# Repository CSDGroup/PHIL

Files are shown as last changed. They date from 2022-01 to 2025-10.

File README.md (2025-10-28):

# PHIL

Pipetting Helper Imaging Lid – PHIL - 2021

Latest Update:
15.05.2022 - Updated Arduino Mega Shield to prevent burnouts by increasing the width of motor power traces:
https://www.pcbway.com/project/shareproject/Arduino_Mega14x_V4_3edde2c7.html

Open-source personal pipetting robots with live-cell incubation and microscopy compatibility

Overview
- personal small desktop liquid handling robot designed in AutoCAD 2018.
- small, light, cheap
- fast self-assembly from 3D printed and commercial parts
- long-term live cell culture media exchange, immunostainings, etc
- compatible with microscope stage-top use during time-lapse microscopy
- user-friendly control software

Reference

If you use PHIL please cite the following paper:

Dettinger*, Dettinger*, Kull, Arekatla, Ahmed, Zhang, Schneiter, Wehling, Schirmacher, Kawamura, Loeffler, Schroeder*
Open-source personal pipetting robots with live-cell incubation and microscopy compatibility
Nature Communications 13, 2999 (2022).
https://doi.org/10.1038/s41467-022-30643-7

System Requirements

Hardware requirements

PHILs GUI requires only a standard computer with enough RAM to support the in-memory operations.

Software requirements

OS Requirements

This package is supported for Windows and requires Matlab 2020. The package has been tested on the following systems:

Windows 10 - Matlab 2020

This project is covered under the MIT License.

Download Files
Current version
PHIL_Complete_Resources_210716.zip (ZIP, 47.2 MB)vertical_align_bottom
2021.07.16: Added companies with international shipping options to «Order_List.xlsx» in PHIL_Complete_Resources.zip

Previous versions
2021.07.05: PHIL_Complete_Resources - .zip (ZIP, 47.2 MB)vertical_align_bottom

ZIP file contents
PHIL operation
PHIL_Operation_Instructions.pdf: Complete instructions for using PHIL
PHIL_GUI_210602.m: Executable Matlab script for PHIL gui

PHIL production
Order_List.xlsx: Complete parts list for all required parts
PHIL_Print_Instructions.pdf: Full print settings of all parts
3D print files as described below
PHIL_Assembly_Instructions.pdf: Full instructions for PHIL assembly
PHIL_Arduino_MEGA_14Pump_210216.ino: Complete Arduino sketch for PHIL operation. Requires Accelstepper library installed
 
3D print files
Individual components are encoded by the individual STL files below. You can use these to print them individually.
All required components for a PHIL robot have been grouped into 10 sets for easy simultaneous printing of several components in one print session.

Set_1.stl
Body_VB1.stl: Main body of PHIL
Body_Top_VB1.stl: Frame for mounting Z-axis stepper motors
Elbow_Left_VB1.stl: Left actuator arm for mounting limit switches
Elbow_Right_VB1.stl: Right actuator arm for mounting limit switches
Hands_VB1.stl: Left and right actuator arm
Tube_Plug_VB1.stl: Tube holder for PHIL body

Set_2.stl
Arm_Plate_VB1.stl: Stepper motor mount for left and right arms
Body_Bottom_VB1.stl: Base for main body of PHIL
 
 
Set_3_100infill.stl
LR_Arm_100Infill.stl: Left and right arms for PHIL. To be printed at 100% infill

Set_4.stl
Chamber _VB1.stl: Incubator chamber
2 x Screw_VB1.stl: Screw drives for z-axis
 
 
Set_5.stl
Chamber_Lid_VB1.stl: Lid for incubator chamber
USB_Back_VB1.stl: USB cable mounting bracket, back
USB_Front_VB1.stl: USB cable mounting bracket, front
Handle_VB1.stl: Handle for power control box
Pin_Cup_V1.stl: Pipet holder for normal wells
(Pin_Cup_V1.stl can be replaced with Pin_Cup_Deep_Well_VB1.stl when working with deep well multiwell plates - see instructions)
 
 
Set_6.stl
Power_Box_Left_VB1.stl: Left half of power control box
 
 
Set_7.stl
Power_Box_Right_VB1.stl: Right half of power control box
 
 
Set_8.stl
Arduino_Plate_VB1.stl: Plate for mounting arduinos
 
 
Set_9.stl
Mount_1x_31.stl: 6x mounting brackets for peristaltic pump
 
 
Set_10.stl
Wheel_1x_31.stl: 6x rotors for peristaltic pump

The following files are not required for a PHIL, but help the production:

tube_bender_top_v2.stl: Tube bending press outer body
tube_bender_bot_v2.stl: Tube bending press inner frame
85mm_Tube_cutter_v2.stl: Jig for cutting 85mm segment of peristaltic pump tubing

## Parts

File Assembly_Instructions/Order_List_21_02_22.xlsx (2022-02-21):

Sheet: Basic Build
Order Type | Supplier | Article No. | Item | Quantity | Price | Total Price | Swiss Order | International Order
Per Robot | 3dware | 1900511.1 | NEMA 17 Stepper motor 1.8 degree, 1.5A 23mm | 4 | 16.95 | 67.8 | https://www.3dware.ch/NEMA-17-Stepper-motor-1.8-degree,-1.5A-23mm-En.htm | https://www.banggood.com/Trianglelab-or-Dforce-Nema-17-23mm-42-Motor-Titan-Stepper-Motor-4-lead-Fits-Extruder-J-head-Bowden-Reprap-for-3D-Printer-p-1845364.ht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
Per Robot | 3dware | 1900354.15 | Power Supply 24v 15A | 1 | 44.95 | 44.95 | https://www.3dware.ch/Power-Supply-24v-15A-En.htm | https://www.banggood.com/Creality-3D-24V-or-15A-Universal-Regulated-Switching-Mode-LED-Power-Supply-For-Ender-3-3D-Printer-p-1335224.html?cur_warehouse=CN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
Per Robot | 3dware | 1900320.4 | StepStick DRV8825 Stepper Motor Driver | 7 | 4.7 | 32.9 | https://www.3dware.ch/StepStick-DRV8825-Stepper-Motor-Driver-En.htm | https://www.banggood.com/Geekcreit-3D-Printer-Stepstick-DRV8825-Stepper-Motor-Driver-Reprap-4-Layer-PCB-p-920162.html?cur_warehouse=CN&rmmds=search
Per Robot | 3dware | 1900824.1 | CH Power Cord 3-pin to C13 | 1 | 5.2 | 5.2 | https://www.3dware.ch/CH-Power-Cord-3-pin-to-C13-En.htm | https://www.banggood.com/AC-Power-Supply-Adapter-Cord-Cable-Lead-3-Prong-for-Laptop-p-930564.html?cur_warehouse=CN&ID=3426&rmmds=search
Per Robot | 3dware | 1900816.3 | Panel mount USB data cable USB type B ma | 1 | 4.7 | 4.7 | https://www.3dware.ch/Panel-mount-USB-data-cable-USB-type-B-male-to-female-50cm-En.htm | https://www.amazon.com/Printer-Extension-Adapter-Connections-Scanner/dp/B071P2BGK5?s=electronics
Per Robot | 3dware | 1900853.1 | Power socket with fuse with wire 10A 250 | 1 | 5.7 | 5.7 | https://www.3dware.ch/Power-socket-with-fuse-with-wire-10A-250V-En.htm | https://www.banggood.com/SIMAX3D-15A-250V-Power-Switch-3pin-AC-Power-Socket-with-Fuse-for-3D-Printer-p-1724703.html?cur_warehouse=CN&ID=6287830&rmmds=search
Per Robot | 3dware | 1900502.6 | NEMA 17 Stepper motor 1.8 degree, 1.5A | 3 | 30.45 | 91.35 | https://www.3dware.ch/NEMA-17-Stepper-motor-1.8-degree,-1.5A-En.htm | https://www.banggood.com/JKM-NEMA17-1_842-Hybrid-Stepper-Motor-Two-Phase-60mm-7_3kg_cm-1_7A-Step-Motor-p-1274866.html?cur_warehouse=CN&rmmds=search
Per Robot | Distrelec | 143-83-920 | Male PCB Header, 36 Contacts, 2.54mm Pitch | 5 | 1.67 | 8.35 | https://www.distrelec.ch/en/890-straight-male-pcb-header-through-hole-rows-36-contacts-54mm-pitch-preci-dip-890-18-036-10-803/p/14383920?track=true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 | https://www.digikey.com/en/products/detail/molex/0022285364/6167155
Per Robot | Distrelec | 135-87-326 | Micro Switch D2F, 3A, 1CO | 4 | 1.91 | 7.64 | https://www.distrelec.ch/en/micro-switch-d2f-3a-1co-47n-hinge-lever-omron-electronic-components-d2f/p/13587326?track=true&no-cache=true&marketingPopup=false | https://www.digikey.com/en/products/detail/omron-electronics-inc-emc-div/D2F-L/83251?s=N4IgTCBcDaIDoBcAiYBiBaAMiAugXyA
Per Robot | Distrelec | 30092030 | Kondensator, 100uF, 50VDC, 20% | 7 | 0.12 | 0.84 | https://www.distrelec.ch/en/radial-electrolytic-capacitor-100uf-50vdc-20-rnd-components-rnd-150ehr101m50b/p/30092030?track=true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 | https://www.digikey.com/en/products/detail/nichicon/UKL1H101MPD1TD/4317601
Per Robot | Distrelec | 30093668 | Female PCB Receptacle, 8 Contacts, 2.54mm Pitch | 14 | 0.15 | 2.1 | https://www.distrelec.ch/en/straight-female-pcb-receptacle-through-hole-rows-contacts-54mm-pitch-rnd-connect-rnd-205-00648/p/30093668?track=true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 | https://www.digikey.com/en/products/detail/sullins-connector-solutions/PPTC081LFBN-RC/810147
Per Robot | Distrelec | 30093662 | Female PCB Receptacle, 2 Contacts, 2.54mm Pitch | 4 | 0.09 | 0.36 | https://www.distrelec.ch/en/straight-female-pcb-receptacle-through-hole-rows-contacts-54mm-pitch-rnd-connect-rnd-205-00642/p/30093662?track=true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 | https://www.digikey.com/en/products/detail/sullins-connector-solutions/PPPC021LFBN-RC/810174
Per Robot | Distrelec | 300-43-058 | Wire-To-Board Terminal Block | 2 | 0.3 | 0.6 | https://www.distrelec.ch/en/wire-to-board-terminal-block-13-31mm-26-16awg-08mm-pitch-poles-rnd-connect-rnd-205-00232/p/30043058?track=true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 | https://www.digikey.com/en/products/detail/phoenix-contact/1733570/348731
Per Robot | digikey | 259-1994-ND | Sunon fans 80mm x 80mm Vapo-Bearing | 1 | 7.76 | 7.76 | https://www.digikey.ch/product-detail/de/sunon-fans/ME80202V3-000U-A99/259-1994-ND/9449330?productid=9449330 | https://www.digikey.com/en/products/detail/sunon-fans/ME80202V3-000U-A99/9449330?s=N4IgTCBcDa4KwE4C0BGBCAsSByAREAugL5A
Per Robot | rs-online.com | 612-5739 | ball bearing id 3mm od 8mm w 4mm | 27 | 5.7 | 153.9 | https://www.modellhubschrauber.ch/Ersatzteile/Elektro/T-Rex-100-760/T-Rex-450/T-Rex-450S-XL/Ersatzteile/Kugellager-693ZZ-3x8x4mm.htm?shop=helibaumann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 | https://www.amazon.com/Miniature-Bearings-Shielded-Bearing-3mm8mm4mm/dp/B0711MRFTY
Per robot | Qosina | 40101 | Female Luer Lock to1/4-28 UNF Thread Connector | 2 | 0.53 | 1.06 |  | https://www.qosina.com/female-luer-lock-connector-white-2-40101
Per 5 Robots | pcbway.com | G662950 | 14 Stepper Motor Arduino Shield | 1 | 25 | 25 |  | https://www.pcbway.com/project/shareproject/14_Stepper_Arduino_Mega_Shield.html
As Necessary | Distrelec | 301-09-228 | No-Clean Solder Wire B2.1 217°C 0.5mm | 1 | 11.18 | 11.18
As Necessary | Reichelt | SDB 2,4 SW | Heat-shrink tubing box, 15 m, black, Ø2.4 mm | 1 |  |  |  | https://www.reichelt.com/ch/en/heat-shrink-tubing-box-15-m-black-2-4-mm-sdb-2-4-sw-p53756.html?CCOUNTRY=459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
Per robot | McMASTER-CARR | 51525K271 | Luer lock to 1/16" barb tube coupling | 2 | 5.18 | 10.36 |  | https://www.mcmaster.com/51525K271/
Per robot | Ismatec | HV-05502-28 | Tygon LMT-55, 1.02 mm ID tubing | 1 | 45.26 | 45.26 |  | https://www.masterflex.com/i/ismatec-pump-tubing-tygon-lmt-55-1-02-mm-id-33-ft/0550228
As Necessary | Fisher Scientific | 11929445 | 30M PTFE TUBE 0.56 X 1.07MM 1.07MM | 1 |  |  |  | https://webshop.fishersci.com/insight2_ch/getProduct.do?productCode=11929445
Per pump | New England Small Tube Corp | NE-1310-03 | Stainless Steel Tube .025“ OD x .013“ ID x 1.00“ Long | 1 |  |  |  | https://www.nesmalltube.com/about_tubing/hypodermic.html
Per robot | Newark | 923050-TE | 23 Gauge, 0.33mm, Needle | 1 | 25.88 | 25.88 |  | https://www.newark.com/metcal/923050-te/needle-23-gauge-orange-0-33mm/dp/93K0393
Per robot | Monster Bolts |  | 8 mm M3 Flat Head Socket Cap screws | 16 |  |  |  | https://monsterbolts.com/products/socket-flat-a2-m3?variant=36305130188
Per robot | Monster Bolts |  | 10 mm M3 Flat Head Socket Cap screws | 3 |  |  |  | https://monsterbolts.com/products/socket-flat-a2-m3?variant=36305130316
Per robot | Monster Bolts |  | 16 mm M3 Flat Head Socket Cap screws | 20 |  |  |  | https://monsterbolts.com/products/socket-flat-a2-m3?variant=36305131020
Per robot | Monster Bolts |  | 10 mm M3 Socket Head Cap screws | 100 |  |  |  | https://monsterbolts.com/products/socket-cap-zn12-9-m3?variant=31330479046739
Per robot | Monster Bolts |  | 20 mm M3 Socket Head Cap screws | 20 |  |  |  | https://monsterbolts.com/products/socket-cap-zn12-9-m3?variant=31330479439955
Per robot | Monster Bolts |  | 2.4 mm thick M3 Hex Nut | 123 |  |  |  | https://monsterbolts.com/collections/nuts-and-locking-nuts/products/nuts-din934-a2?variant=36167130316
Per robot | Uxcell | US-SA-AJD-353837 | M1.5 X 10mm Stainless Steel Phillips Pan Round Head Self Tapping Screws | 8 |  |  |  | https://www.amazon.com/uxcell-Stainless-Phillips-Tapping-Screws/dp/B01KXTTT22
 |  |  |  |  |  | 552.89

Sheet: Full Build
Order Type | Supplier | Article No. | Item | Quantity | Price | Total Price | Swiss Order | International Order
Per Robot | 3dware | 1900511.1 | NEMA 17 Stepper motor 1.8 degree, 1.5A 23mm | 4 | 16.95 | 67.8 | https://www.3dware.ch/NEMA-17-Stepper-motor-1.8-degree,-1.5A-23mm-En.htm | https://www.banggood.com/Trianglelab-or-Dforce-Nema-17-23mm-42-Motor-Titan-Stepper-Motor-4-lead-Fits-Extruder-J-head-Bowden-Reprap-for-3D-Printer-p-1845364.ht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
Per Robot | 3dware | 1900354.15 | Power Supply 24v 15A | 1 | 44.95 | 44.95 | https://www.3dware.ch/Power-Supply-24v-15A-En.htm | https://www.banggood.com/Creality-3D-24V-or-15A-Universal-Regulated-Switching-Mode-LED-Power-Supply-For-Ender-3-3D-Printer-p-1335224.html?cur_warehouse=CN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
Per Robot | 3dware | 1900320.4 | StepStick DRV8825 Stepper Motor Driver | 14 | 4.7 | 65.8 | https://www.3dware.ch/StepStick-DRV8825-Stepper-Motor-Driver-En.htm | https://www.banggood.com/Geekcreit-3D-Printer-Stepstick-DRV8825-Stepper-Motor-Driver-Reprap-4-Layer-PCB-p-920162.html?cur_warehouse=CN&rmmds=search
Per Robot | 3dware | 1900824.1 | CH Power Cord 3-pin to C13 | 1 | 5.2 | 5.2 | https://www.3dware.ch/CH-Power-Cord-3-pin-to-C13-En.htm | https://www.banggood.com/AC-Power-Supply-Adapter-Cord-Cable-Lead-3-Prong-for-Laptop-p-930564.html?cur_warehouse=CN&ID=3426&rmmds=search
Per Robot | 3dware | 1900816.3 | Panel mount USB data cable USB type B ma | 1 | 4.7 | 4.7 | https://www.3dware.ch/Panel-mount-USB-data-cable-USB-type-B-male-to-female-50cm-En.htm | https://www.amazon.com/Printer-Extension-Adapter-Connections-Scanner/dp/B071P2BGK5?s=electronics
Per Robot | 3dware | 1900853.1 | Power socket with fuse with wire 10A 250 | 1 | 5.7 | 5.7 | https://www.3dware.ch/Power-socket-with-fuse-with-wire-10A-250V-En.htm | https://www.banggood.com/SIMAX3D-15A-250V-Power-Switch-3pin-AC-Power-Socket-with-Fuse-for-3D-Printer-p-1724703.html?cur_warehouse=CN&ID=6287830&rmmds=search
Per Robot | 3dware | 1900502.6 | NEMA 17 Stepper motor 1.8 degree, 1.5A | 10 | 30.45 | 304.5 | https://www.3dware.ch/NEMA-17-Stepper-motor-1.8-degree,-1.5A-En.htm | https://www.banggood.com/JKM-NEMA17-1_842-Hybrid-Stepper-Motor-Two-Phase-60mm-7_3kg_cm-1_7A-Step-Motor-p-1274866.html?cur_warehouse=CN&rmmds=search
Per Robot | Distrelec | 143-83-920 | Male PCB Header, 36 Contacts, 2.54mm Pitch | 5 | 1.67 | 8.35 | https://www.distrelec.ch/en/890-straight-male-pcb-header-through-hole-rows-36-contacts-54mm-pitch-preci-dip-890-18-036-10-803/p/14383920?track=true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 | https://www.digikey.com/en/products/detail/molex/0022285364/6167155
Per Robot | Distrelec | 135-87-326 | Micro Switch D2F, 3A, 1CO | 4 | 1.91 | 7.64 | https://www.distrelec.ch/en/micro-switch-d2f-3a-1co-47n-hinge-lever-omron-electronic-components-d2f/p/13587326?track=true&no-cache=true&marketingPopup=false | https://www.digikey.com/en/products/detail/omron-electronics-inc-emc-div/D2F-L/83251?s=N4IgTCBcDaIDoBcAiYBiBaAMiAugXyA
Per Robot | Distrelec | 30092030 | Kondensator, 100uF, 50VDC, 20% | 14 | 0.12 | 1.68 | https://www.distrelec.ch/en/radial-electrolytic-capacitor-100uf-50vdc-20-rnd-components-rnd-150ehr101m50b/p/30092030?track=true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 | https://www.digikey.com/en/products/detail/nichicon/UKL1H101MPD1TD/4317601
Per Robot | Distrelec | 30093668 | Female PCB Receptacle, 8 Contacts, 2.54mm Pitch | 28 | 0.15 | 4.2 | https://www.distrelec.ch/en/straight-female-pcb-receptacle-through-hole-rows-contacts-54mm-pitch-rnd-connect-rnd-205-00648/p/30093668?track=true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 | https://www.digikey.com/en/products/detail/sullins-connector-solutions/PPTC081LFBN-RC/810147
Per Robot | Distrelec | 30093662 | Female PCB Receptacle, 2 Contacts, 2.54mm Pitch | 4 | 0.09 | 0.36 | https://www.distrelec.ch/en/straight-female-pcb-receptacle-through-hole-rows-contacts-54mm-pitch-rnd-connect-rnd-205-00642/p/30093662?track=true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 | https://www.digikey.com/en/products/detail/sullins-connector-solutions/PPPC021LFBN-RC/810174
Per Robot | Distrelec | 300-43-058 | Wire-To-Board Terminal Block | 2 | 0.3 | 0.6 | https://www.distrelec.ch/en/wire-to-board-terminal-block-13-31mm-26-16awg-08mm-pitch-poles-rnd-connect-rnd-205-00232/p/30043058?track=true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 | https://www.digikey.com/en/products/detail/phoenix-contact/1733570/348731
Per Robot | digikey | 259-1994-ND | Sunon fans 80mm x 80mm Vapo-Bearing | 1 | 7.76 | 7.76 | https://www.digikey.ch/product-detail/de/sunon-fans/ME80202V3-000U-A99/259-1994-ND/9449330?productid=9449330 | https://www.digikey.com/en/products/detail/sunon-fans/ME80202V3-000U-A99/9449330?s=N4IgTCBcDa4KwE4C0BGBCAsSByAREAugL5A
Per Robot | rs-online.com | 612-5739 | ball bearing id 3mm od 8mm w 4mm | 83 | 5.7 | 473.1 | https://www.modellhubschrauber.ch/Ersatzteile/Elektro/T-Rex-100-760/T-Rex-450/T-Rex-450S-XL/Ersatzteile/Kugellager-693ZZ-3x8x4mm.htm?shop=helibaumann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 | https://www.amazon.com/Miniature-Bearings-Shielded-Bearing-3mm8mm4mm/dp/B0711MRFTY
Per robot | Qosina | 40101 | Female Luer Lock to1/4-28 UNF Thread Connector | 2 | 0.53 | 1.06 |  | https://www.qosina.com/female-luer-lock-connector-white-2-40101
Per 5 Robots | pcbway.com | G662950 | 14 Stepper Motor Arduino Shield | 1 | 25 | 25 |  | https://www.pcbway.com/project/shareproject/14_Stepper_Arduino_Mega_Shield.html
As Necessary | Distrelec | 301-09-228 | No-Clean Solder Wire B2.1 217°C 0.5mm | 1 | 11.18 | 11.18
As Necessary | Reichelt | SDB 2,4 SW | Heat-shrink tubing box, 15 m, black, Ø2.4 mm | 1 |  |  |  | https://www.reichelt.com/ch/en/heat-shrink-tubing-box-15-m-black-2-4-mm-sdb-2-4-sw-p53756.html?CCOUNTRY=459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
Per robot | McMASTER-CARR | 51525K271 | Luer lock to 1/16" barb tube coupling | 2 | 5.18 | 10.36 |  | https://www.mcmaster.com/51525K271/
Per robot | Ismatec | HV-05502-28 | Tygon LMT-55, 1.02 mm ID tubing | 1 | 45.26 | 45.26 |  | https://www.masterflex.com/i/ismatec-pump-tubing-tygon-lmt-55-1-02-mm-id-33-ft/0550228
As Necessary | Fisher Scientific | 11929445 | 30M PTFE TUBE 0.56 X 1.07MM 1.07MM | 1 |  |  |  | https://webshop.fishersci.com/insight2_ch/getProduct.do?productCode=11929445
Per pump | New England Small Tube Corp | NE-1310-03 | Stainless Steel Tube .025“ OD x .013“ ID x 1.00“ Long | 1 |  |  |  | https://www.nesmalltube.com/about_tubing/hypodermic.html
Per robot | Newark | 923050-TE | 23 Gauge, 0.33mm, Needle | 1 | 25.88 | 25.88 |  | https://www.newark.com/metcal/923050-te/needle-23-gauge-orange-0-33mm/dp/93K0393
Per robot | Monster Bolts |  | 8 mm M3 Flat Head Socket Cap screws | 16 |  |  |  | https://monsterbolts.com/products/socket-flat-a2-m3?variant=36305130188
Per robot | Monster Bolts |  | 10 mm M3 Flat Head Socket Cap screws | 3 |  |  |  | https://monsterbolts.com/products/socket-flat-a2-m3?variant=36305130316
Per robot | Monster Bolts |  | 16 mm M3 Flat Head Socket Cap screws | 20 |  |  |  | https://monsterbolts.com/products/socket-flat-a2-m3?variant=36305131020
Per robot | Monster Bolts |  | 10 mm M3 Socket Head Cap screws | 100 |  |  |  | https://monsterbolts.com/products/socket-cap-zn12-9-m3?variant=31330479046739
Per robot | Monster Bolts |  | 20 mm M3 Socket Head Cap screws | 20 |  |  |  | https://monsterbolts.com/products/socket-cap-zn12-9-m3?variant=31330479439955
Per robot | Monster Bolts |  | 2.4 mm thick M3 Hex Nut | 123 |  |  |  | https://monsterbolts.com/collections/nuts-and-locking-nuts/products/nuts-din934-a2?variant=36167130316
Per robot | Uxcell | US-SA-AJD-353837 | M1.5 X 10mm Stainless Steel Phillips Pan Round Head Self Tapping Screws | 8 |  |  |  | https://www.amazon.com/uxcell-Stainless-Phillips-Tapping-Screws/dp/B01KXTTT22

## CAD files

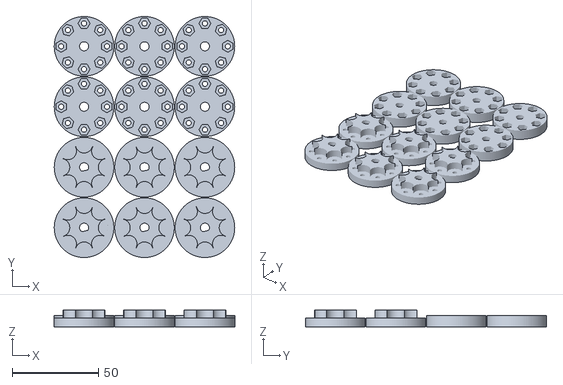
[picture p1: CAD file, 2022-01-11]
PHIL_Printable_Files/PHIL_Grouped_Components/Wheel_31.stl
104.5 x 139.5 x 9.62

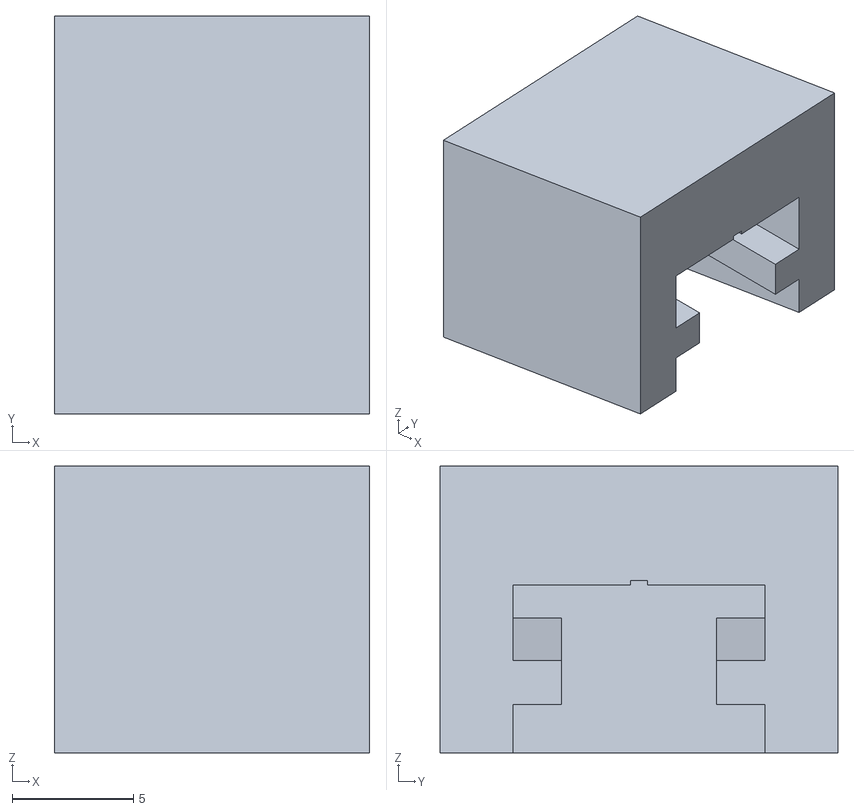
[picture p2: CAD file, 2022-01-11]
PHIL_Printable_Files/PHIL_Individual_Components/PHIL_Accessories/tube_bender_top_v2.stl
13.0 x 16.4 x 11.8

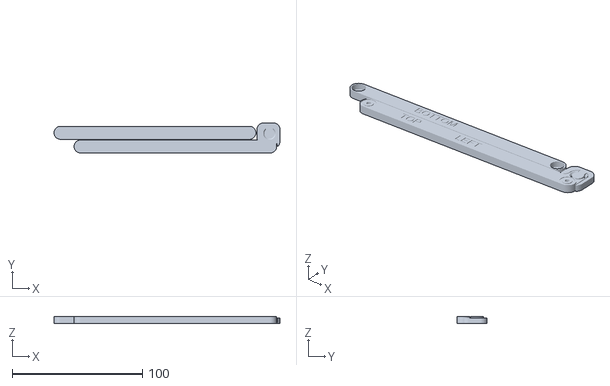
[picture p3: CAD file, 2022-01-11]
PHIL_Printable_Files/PHIL_Individual_Components/PHIL_Body/Hands_VB1.stl
173.4 x 23.1 x 5.00

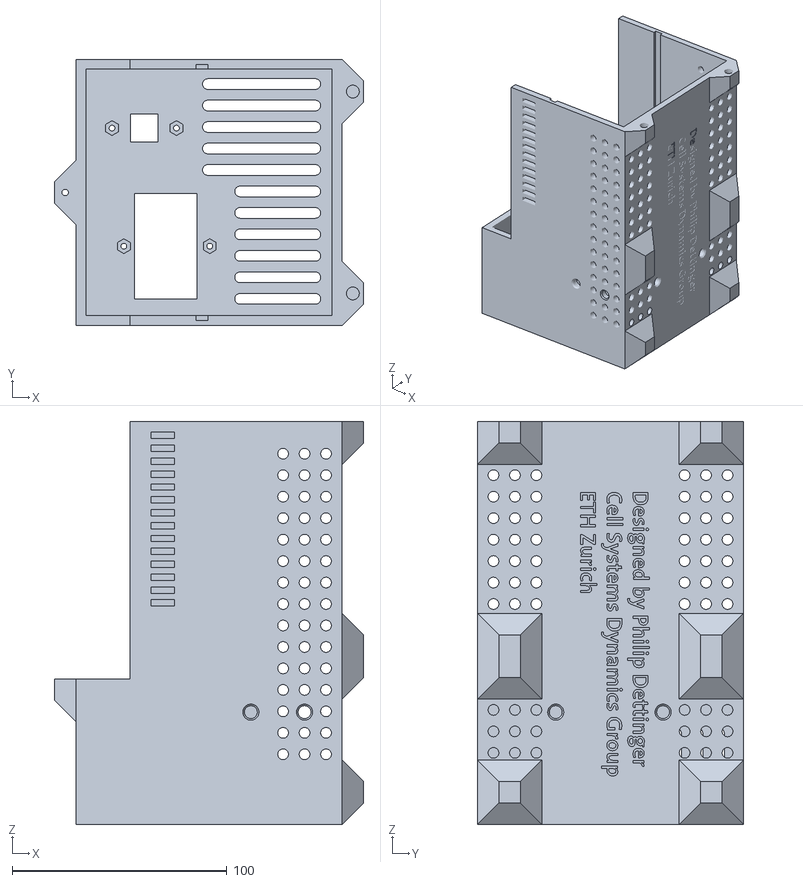
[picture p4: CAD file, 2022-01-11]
PHIL_Printable_Files/PHIL_Individual_Components/PHIL_Power_Supply/Power_Box_Left_VB1.stl
144.0 x 124.0 x 187.7

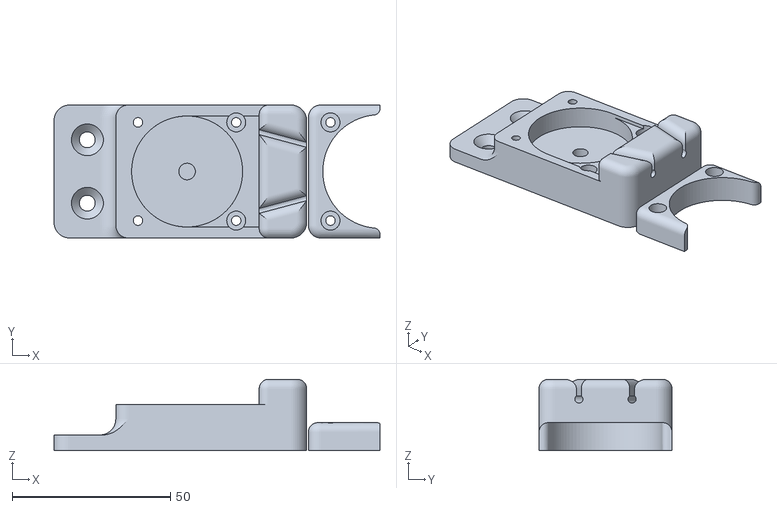
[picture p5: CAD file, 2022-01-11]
PHIL_Printable_Files/PHIL_Individual_Components/PHIL_Pumps/Mount_1x_31.stl
102.9 x 42.0 x 22.6

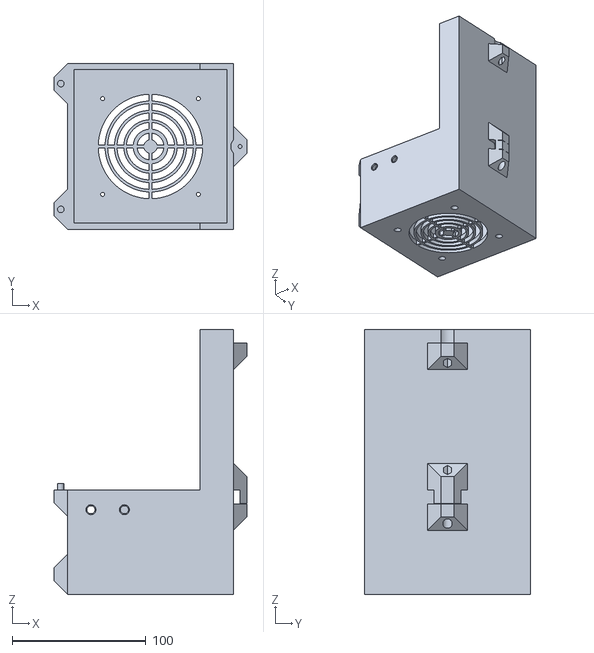
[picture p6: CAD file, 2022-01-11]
PHIL_Printable_Files/PHIL_Grouped_Components/Set_7.stl
144.0 x 124.0 x 198.0

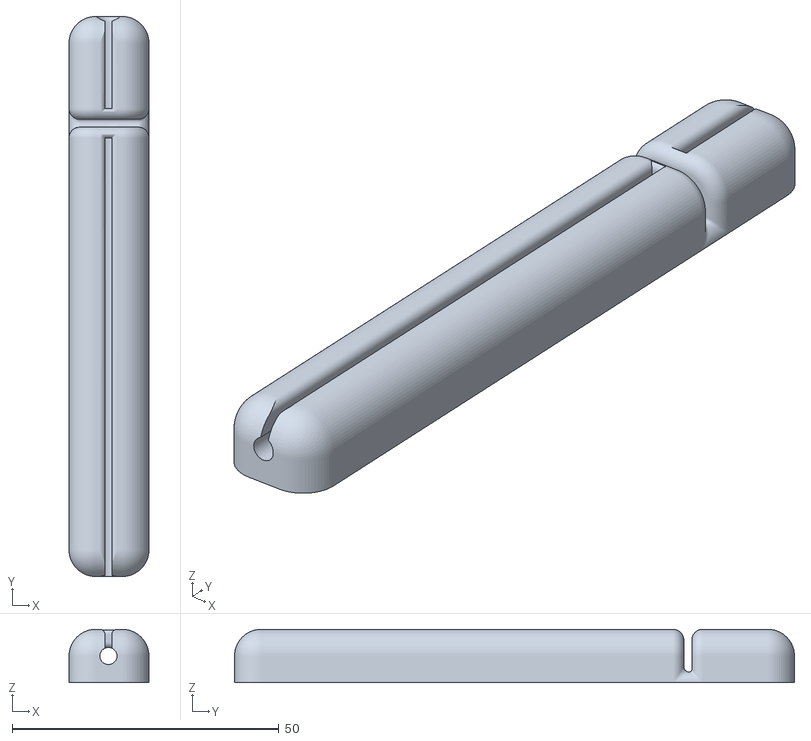
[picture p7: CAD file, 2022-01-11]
PHIL_Printable_Files/PHIL_Individual_Components/PHIL_Accessories/85mm_Tube_cutter_v2.stl
15.0 x 105.0 x 10.0

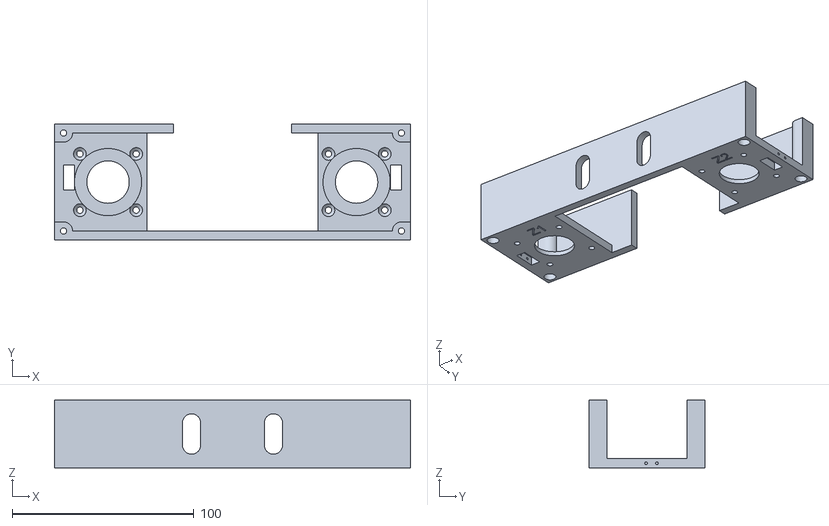
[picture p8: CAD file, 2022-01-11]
PHIL_Printable_Files/PHIL_Individual_Components/PHIL_Body/Body_Top_VB1.stl
196.1 x 64.0 x 37.2

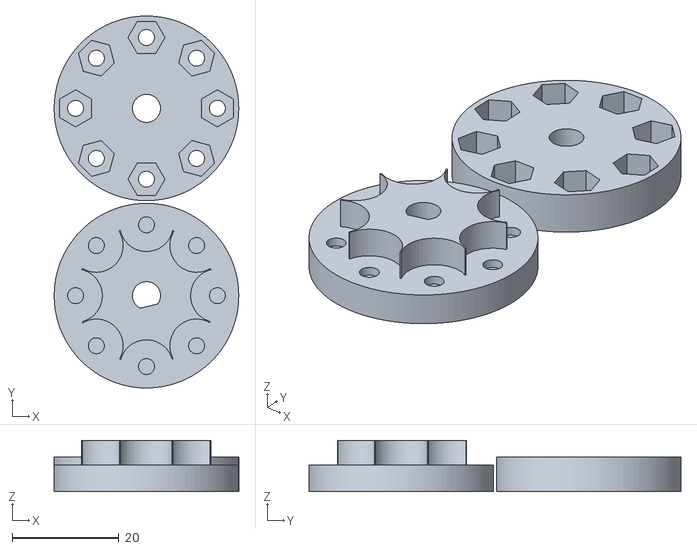
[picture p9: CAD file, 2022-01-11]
PHIL_Printable_Files/PHIL_Individual_Components/PHIL_Pumps/Wheel_1x_31.stl
34.5 x 69.5 x 9.62

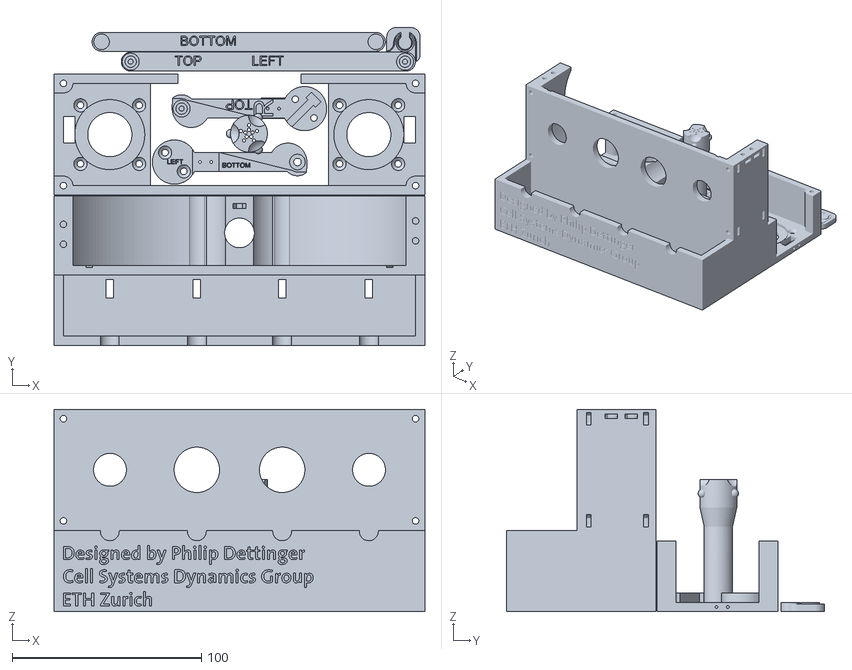
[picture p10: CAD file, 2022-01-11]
PHIL_Printable_Files/PHIL_Grouped_Components/Set_1.stl
196.1 x 168.1 x 107.0

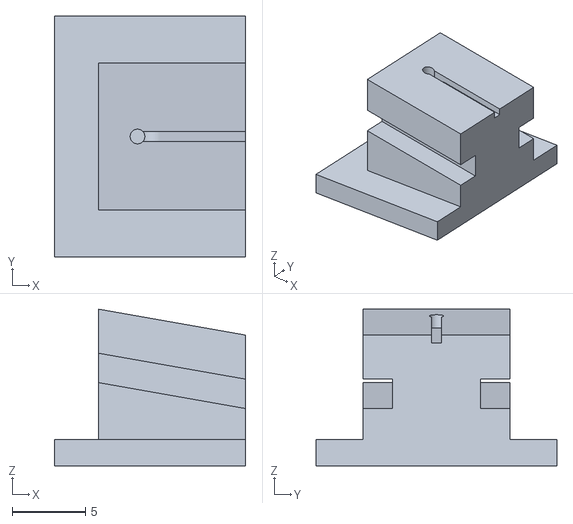
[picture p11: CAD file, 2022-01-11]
PHIL_Printable_Files/PHIL_Individual_Components/PHIL_Accessories/tube_bender_bot_v2.stl
13.0 x 16.4 x 10.7

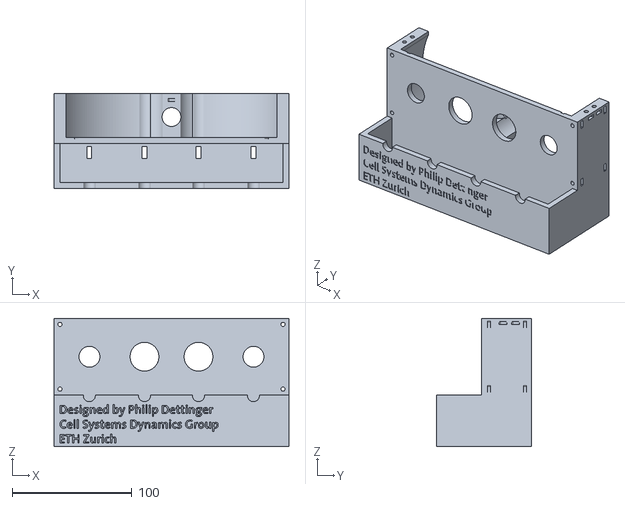
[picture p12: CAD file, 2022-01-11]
PHIL_Printable_Files/PHIL_Individual_Components/PHIL_Body/Body_VB1.stl
196.1 x 79.0 x 107.0

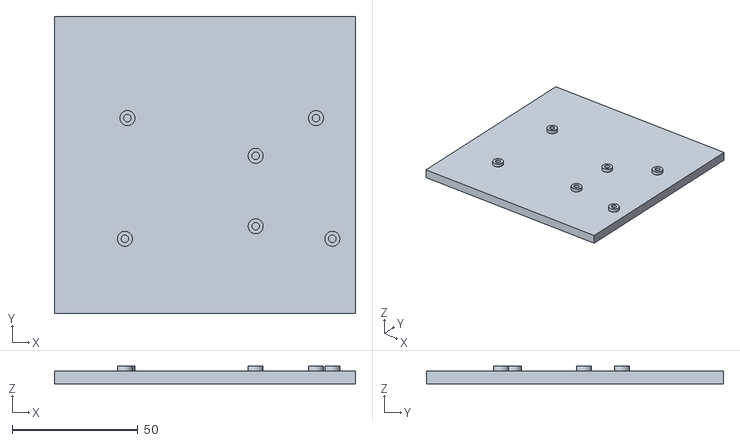
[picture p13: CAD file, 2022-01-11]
PHIL_Printable_Files/PHIL_Individual_Components/PHIL_Power_Supply/Arduino_Plate_VB1.stl
119.7 x 118.3 x 7.00

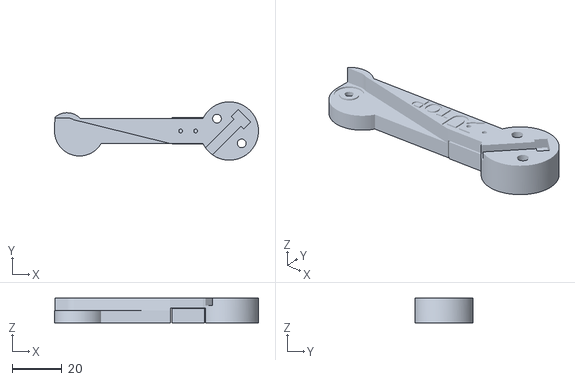
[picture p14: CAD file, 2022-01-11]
PHIL_Printable_Files/PHIL_Individual_Components/PHIL_Body/Elbow_Right_VB1.stl
81.7 x 23.3 x 10.00

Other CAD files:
PHIL_Printable_Files/PHIL_Individual_Components/PHIL_Power_Supply/Power_Box_Right_VB1.stl
PHIL_Printable_Files/PHIL_Individual_Components/PHIL_Power_Supply/USB_Back_VB1.stl
PHIL_Printable_Files/PHIL_Grouped_Components/Mount_31.stl
PHIL_Original_Files/210104_PD_Power_Control_Box.dwg
PHIL_Original_Files/210312_PD_Syringe_Pump.dwg
PHIL_Printable_Files/PHIL_Grouped_Components/Set_2.stl
PHIL_Printable_Files/PHIL_Grouped_Components/Set_3_100Infill.stl
PHIL_Printable_Files/PHIL_Grouped_Components/Set_4.stl
PHIL_Printable_Files/PHIL_Grouped_Components/Set_5.stl
PHIL_Printable_Files/PHIL_Individual_Components/PHIL_Body/Chamber_Lid_VB1.stl
PHIL_Printable_Files/PHIL_Individual_Components/PHIL_Body/Chamber_VB1.stl
PHIL_Printable_Files/PHIL_Individual_Components/PHIL_Body/Elbow_Left_VB1.stl
PHIL_Printable_Files/PHIL_Individual_Components/PHIL_Body/Screw_VB1.stl
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

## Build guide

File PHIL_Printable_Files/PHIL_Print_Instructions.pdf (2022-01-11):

Print all sets with:
- 3 walls
- .15 mm layer height
Print sets 1,2,4-10 with
- 20% infill
Print set 3 with:
- 100% infill
Set 1

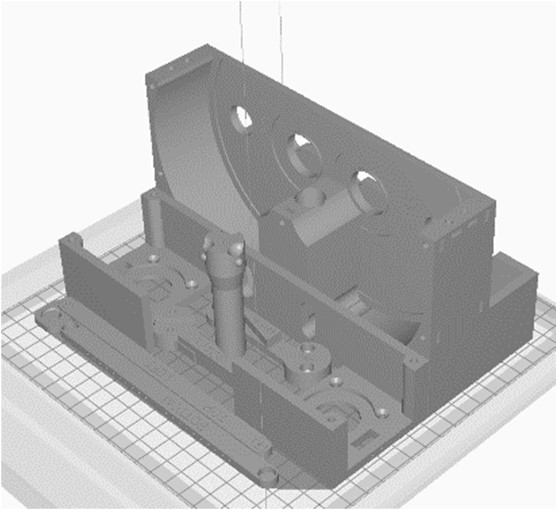
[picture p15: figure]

Set 2

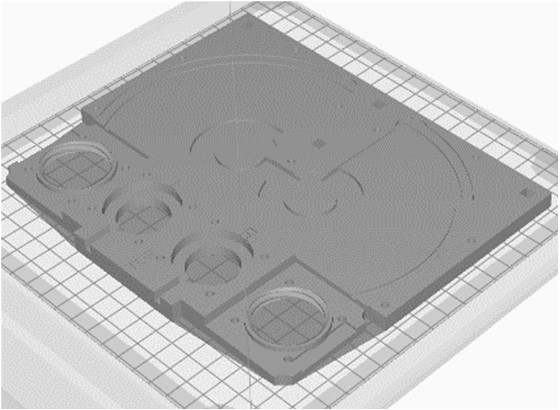
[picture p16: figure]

Set 3

Set 4

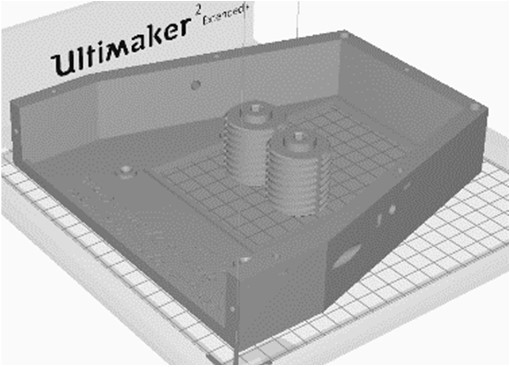
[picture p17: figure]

Set 5

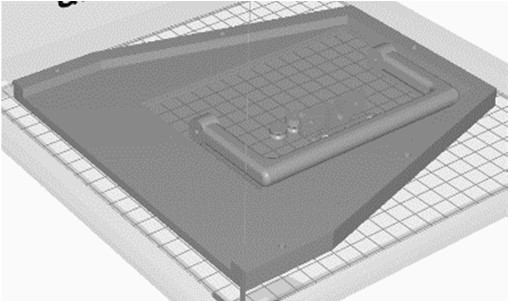
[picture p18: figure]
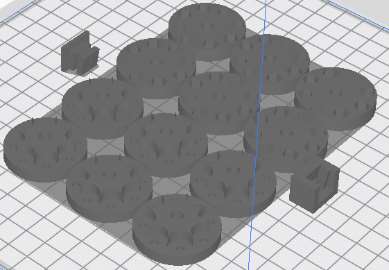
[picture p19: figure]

Set 6

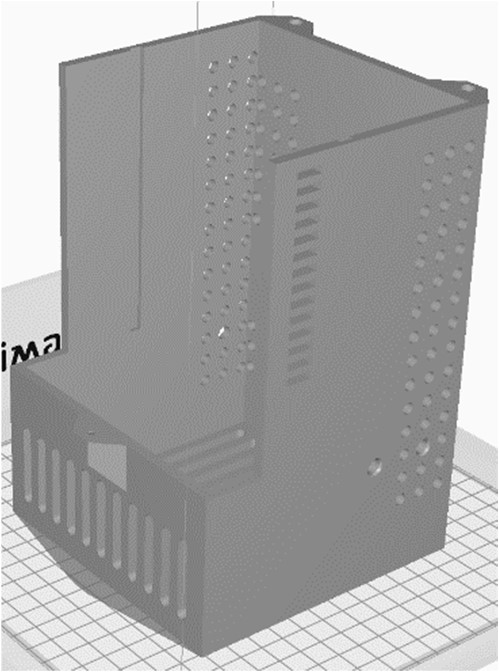
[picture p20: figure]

Set 7

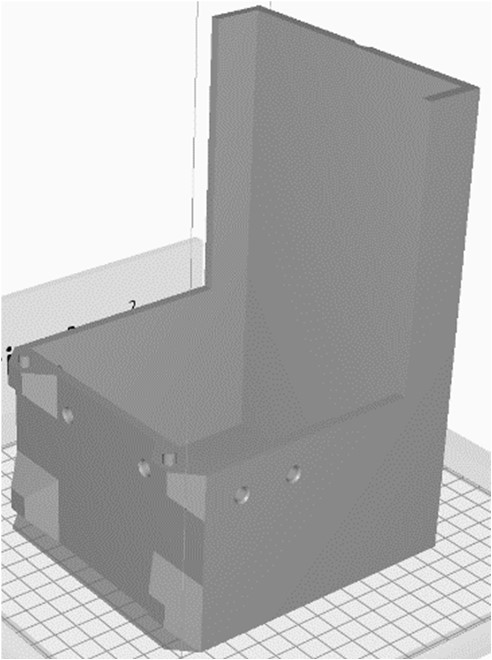
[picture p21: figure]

Set 8

Set 9

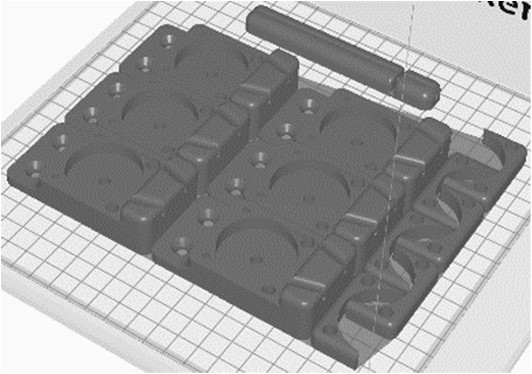
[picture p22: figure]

Set 10

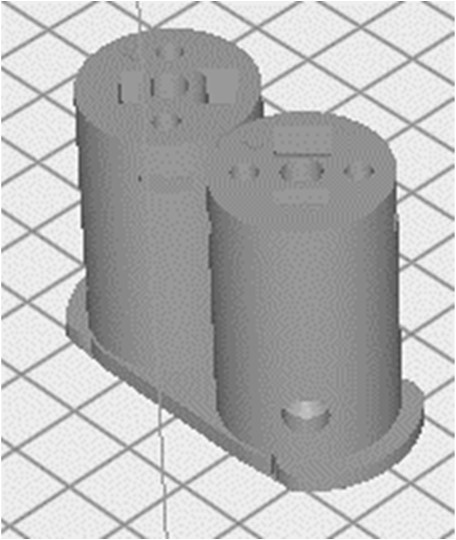
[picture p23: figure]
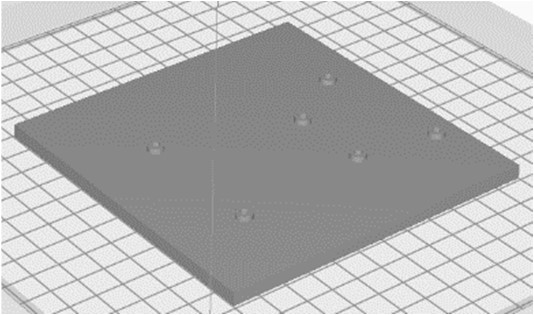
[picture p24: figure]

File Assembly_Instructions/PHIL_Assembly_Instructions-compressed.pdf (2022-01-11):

### 1. PHiL Assembly Instructions

a. Main Body
i. Assemble Limit Switches

### 1. Solder 15cm long red and black wires to 4 limit switches as shown below (See

Appendix 1: Basic Soldering).

2. Place 1cm long x 2mm diameter heat shrink tubing over soldered joints.
3. Apply air gun at 300°C to all heat shrink segments for 5-6s as shown below.
a. Safety Note: The airgun tip is extremely hot. Do not touch it with unprotected skin or place it on combustible objects.

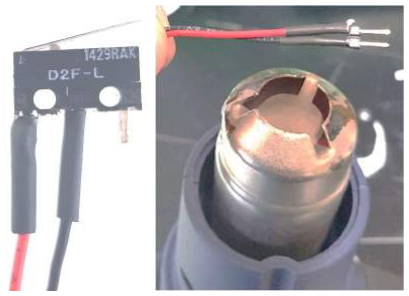
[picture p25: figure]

4. Place 1cm long x 2mm diameter heat shrink tubing over each wire.
5. Solder 15cm long red and black wires to 4 male headers as shown below.

### 6. Move 1cm long x 2mm diameter heat shrink tubing over each joint and shrink with

air gun.
ii. Assemble Arm Platform
a. Supplies:
i. M3 nut x 28
ii. 8mm M3 screw x 20
iii. 10mm M3 screw x 7
iv. 16mm M3 screw x 21
v. 8mm bearing x 3

vi. 10mm M1.5 screw x 8

2. Insert 1 M3 nut into the vertical cavity of the Arm columns as shown below.
3. Push 1 limit switch connector through each Arm Column as shown below.

### 4. Insert 1 stepper motor shaft in each Arm Column and attach securely using 4x 8mm

M3 screws as shown below.
a. Note: Stepper motor shafts have a flat face which aligns with the square cut in the Arm Column sleeve. Some force may be required.

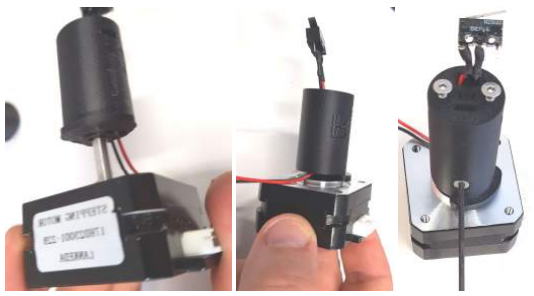
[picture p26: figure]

### 5. Attach each stepper motor to the Arm Platform using 4x 8mm M3 screws as shown

below.

a. Note: Each motor receives its own limit switch.
b. Note: Align the back of each stepper motor with the back of the Arm Platform as seen in the photo.

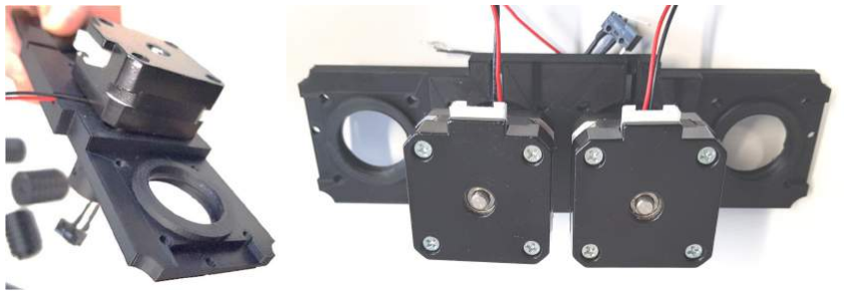
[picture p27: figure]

iii. Install Z-axis Limit Switches

### 1. Insert 1 limit switch in each Z-axis slot and fix in place with 2x 10mm M1.5 screws as

shown below.
a. Note: Each motor receives its own limit switch.
b. Note: Some limit switch movement may be required to align the screws with the mounting holes in the limit switch bodies. Simply move the limit switches up and down until each screw turns easily.

iv. Install Z-axis Stepper Motors
1. Insert 1 stepper motor in each side of the Z-axis mounting bracket as shown below.
a. Note: Align the back of each stepper motor with the back of the Z-axis bracket as seen in the photo.
2. Attach each stepper motor to the Z-axis bracket using 4x 8mm M3 screws.
3. Insert 1 M3 nut into the vertical cavity of each Lead Screw as shown below.

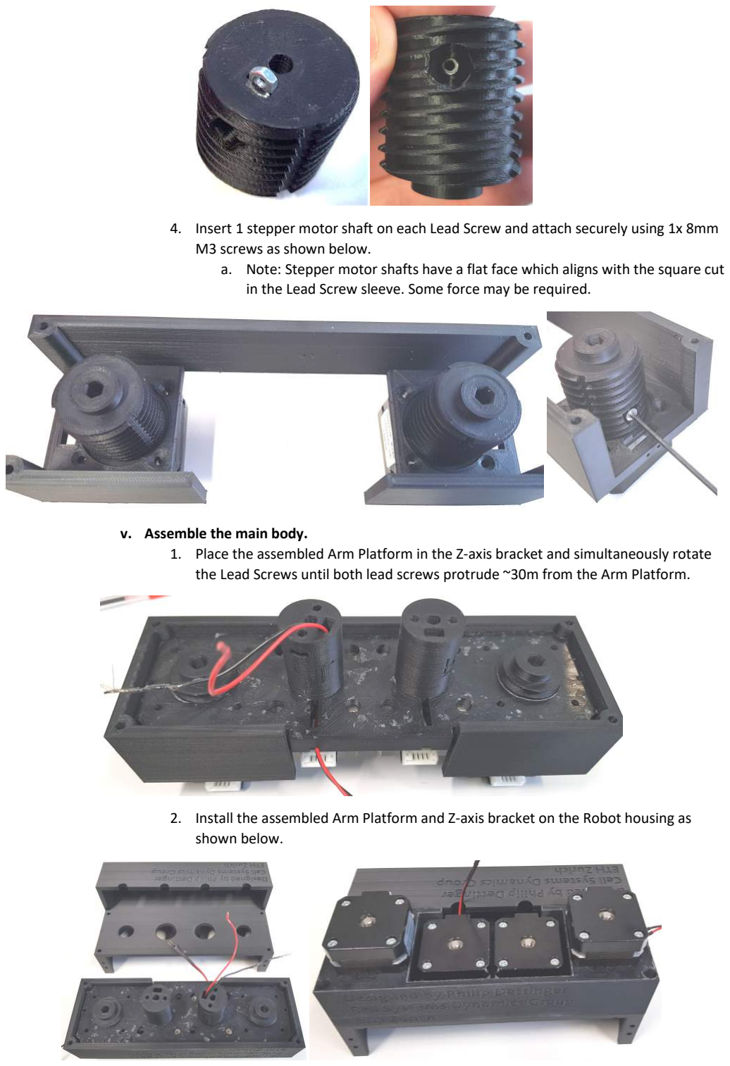
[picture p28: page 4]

### 4. Insert 1 stepper motor shaft on each Lead Screw and attach securely using 1x 8mm

M3 screws as shown below.
a. Note: Stepper motor shafts have a flat face which aligns with the square cut in the Lead Screw sleeve. Some force may be required.
v. Assemble the main body.

### 1. Place the assembled Arm Platform in the Z-axis bracket and simultaneously rotate

the Lead Screws until both lead screws protrude ~30m from the Arm Platform.

### 2. Install the assembled Arm Platform and Z-axis bracket on the Robot housing as

shown below.

3. Insert 1 M3 nut in each cavity of the main body as shown below.

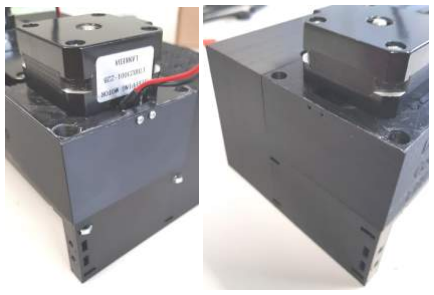
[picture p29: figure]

### 4. Fix the assembled Arm Platform and Z-axis bracket to the main body using 4x 16mm

M3 screws as shown below.

vi. Install Left and Right Arms

### 1. Align the limit switch mounting holes with the corresponding holes in the left and

right Arm pivots and fix in place with 2x 10mm M1.5 screws as shown below.
a. Note: Play close attention to the orientation of the limit switch. The metal lever should point away from the circular base and the slot for the wires depicted in the photo below.
2. Insert 1 M3 nut in each cavity of the Arm columns as shown below.

### 3. Loosely fix the Arm columns to the Arm pivot using 2x 16mm M3 screws as shown

below.
a. Note: Each component is labelled with a letter for its corresponding side. ie L for left and R for right.

### 4. Align limit switch wires with the wire channel before fully tightening the Arm pivot

screws as shown below.

### 5. Gently pull the limit switch wires through the assembled Arm column and Arm pivot

until tight as shown below.

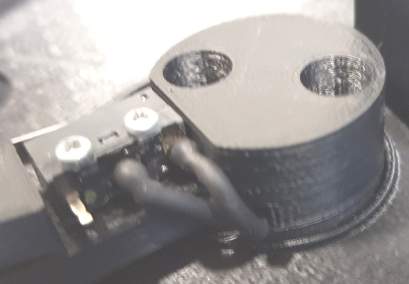
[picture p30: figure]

i. Install Manipulators

6. Place 1x M3 nut in each hexagonal hole of the left and right Manipulator.

### 7. Place 1x 8mm bearing in each circular hole of the left and right Arm pivots as well as

the right Manipulator as shown below.

### 8. Fix the left and right manipulators to the corresponding Arm pivot using 1x 10mm

M3 screws as shown below.

### 9. Fix the left and right manipulators to each other using 1x 10mm M3 screws as shown

below.

ii. Install main body base
10. Insert 1 M3 nut in each cavity of the main body as shown below.

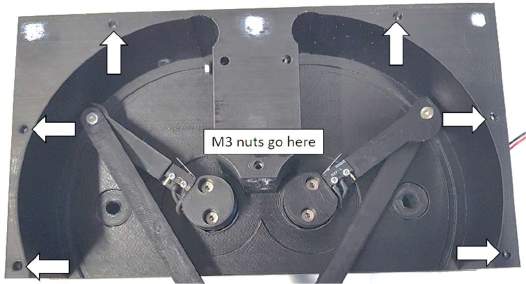
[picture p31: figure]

11. Insert 1 M3 nut in each cavity of the main body as shown below.

12. Fix the main body base to the main body using 6x 16mm M3 screws as shown below.
b. Incubation Chamber
i. Assemble Base
1. Insert 1x M3 nut into the horizontal cavities of the chamber body as shown below.
2. Place 1x 16mm M3 screw in each mounting cavity as shown below.
3. Screw gas connector into connection holes as shown below.

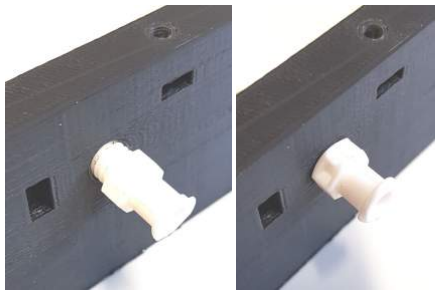
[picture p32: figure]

4. Attach Chamber lid to chamber body using 20mm M3 screws as shown below.
c. Peristaltic Pumps
i. Assemble Peristaltic Pump Wheel
a. Supplies
i. Wheel Bottom x 1
ii. Wheel Top x 1
iii. M3 Nut x 8
iv. 10mm M3 screw x 8
v. 8mm Bearing x 8
2. Place 10mm M3 screws in Wheel Top holes as shown below.

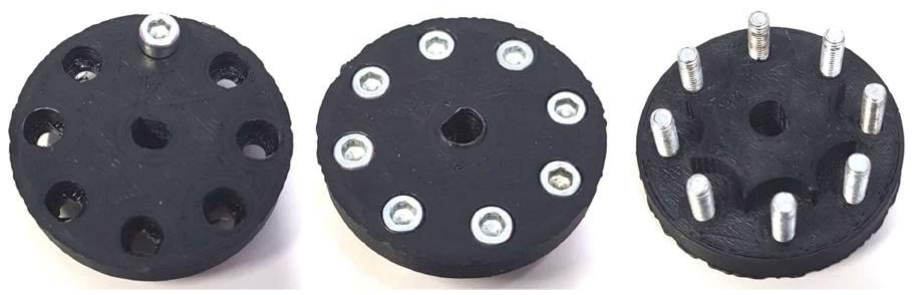
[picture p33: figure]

3. Place 8mm Bearings on 10mm M3 Screws as shown below.
4. Place Wheel Bottom over Wheel Top and install M3 nuts as shown below.
a. Note: After tightening all 10mm M3 Crews loosen each until the ball bearing spins freely.

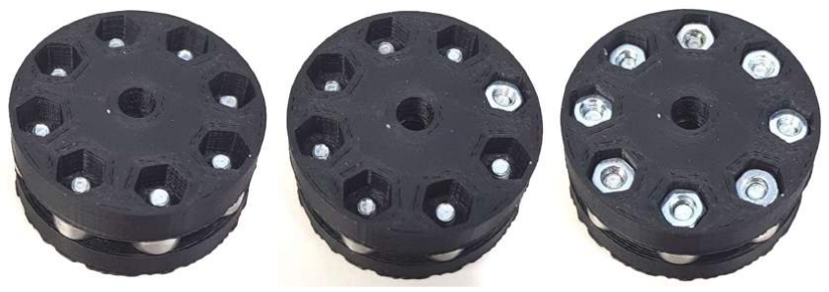
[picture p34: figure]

ii. Assemble Pump Tubing
a. Supplies:
i. Tygon LMT-55 Tubing
ii. 1/16” Barb Femal connector iii. Scalpel
iv. 85mm Tube Cutting Jig

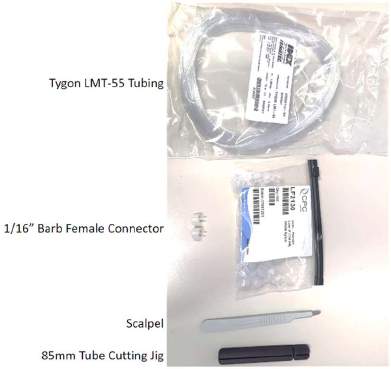
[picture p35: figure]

### 2. Cut Tygon LMT-55 Tubing into 85mm segment using the Tube Cutting Jig as shown

below.

3. Attach 1/16” barb to each end of 85mm tube segment as shown below.

iii. Assemble Peristaltic Pump Mount
a. Supplies
i. Nema 17 Stepper Motor x 1 ii. Peristaltic Pump Mount x 1 iii. Peristaltic Pump Bracket x 1 iv. 10mm M3 Screw x 2
v. 20mm M3 Screw x 2

### 2. Place Peristaltic Pump Mount onto Nema 17 Stepper Motor and attach it with 10mm

M3 Screws as shown below.

3. Place Assembled Wheel on Nema 17 Stepper motor shaft as shown below.
a. Note: The flat edge of the wheel should match the flat edge of the Nema 17 Stepper Motor.
4. Place assembled Peristaltic Pump Tube in grooves as shown below.

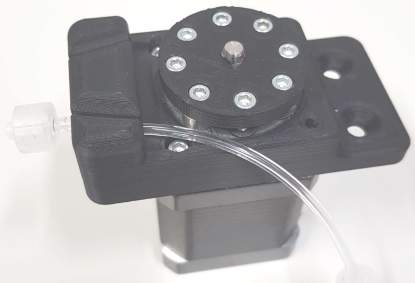
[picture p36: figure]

### 5. Stretch Peristaltic Pump Tube around the Wheel and through the second groove in

the Peristaltic Pump Mount as shown below.

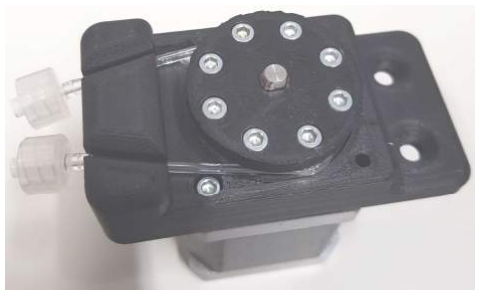
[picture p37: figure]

6. Place Peristaltic Pump bracket around tubing and wheel as shown below.

### 7. Attach Peristaltic Pump Bracket to Nema 17 Stepper Motor using 20mm M3 Screws

as shown below.
a. Note: You must apply pressure to the bracket to push it towards the wheel in order to align the holes for the screw.

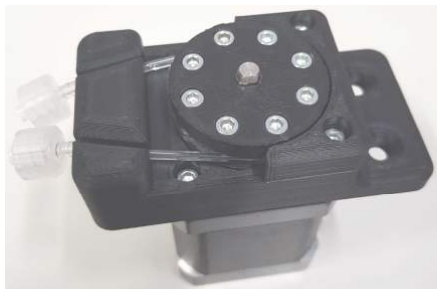
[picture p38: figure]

8. Repeat all steps for each Pump you wish to use.
d. Control Box
i. Assemble Arduino Shield

### 1. Gather 1x Arduino Mega, 5x 8 pin male header, 1x 6 pin male header, & 2x 18 pin

male headers as shown below.

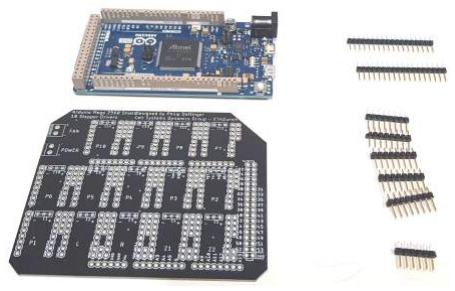
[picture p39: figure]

### 2. Insert the long end of each header into the female headers of the Arduino Mega as

seen below.

### 3. Place the Shield onto the Arduino Mega such that the male headers fit in the

appropriate holes as shown below.

4. Solder each pin into place as shown below.
5. Place 8 pin female headers onto a stepper driver board as shown below.

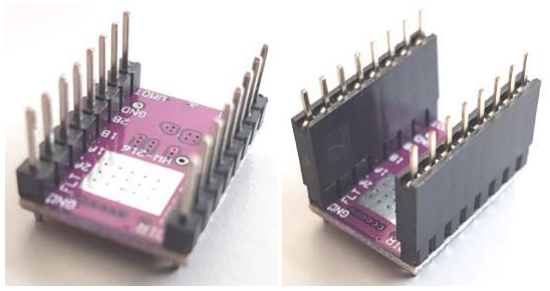
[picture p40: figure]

### 6. Place each stepper driver board into the shield holes then flip the board upside

down using a clear plastic sheet to hold them in place as shown below.

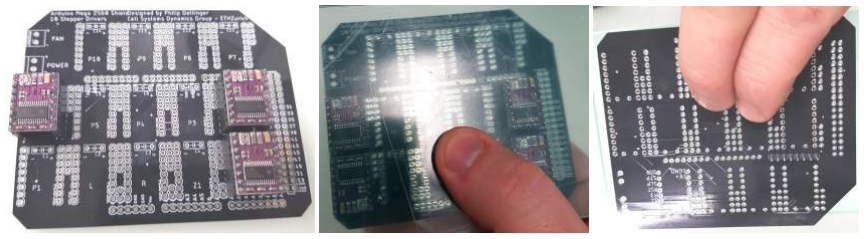
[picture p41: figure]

7. Solder stepper driver shields in place as shown below.
8. Repeat steps 6 & 7 for all stepper driver positions shown below.

### 9. Place 4 pin & 2 pin female headers adjacent to stepper driver headers and hold

them in place using 2 pin male headers then solder them to the bottom of the board as shown below.

10. Repeat step 9 for all stepper driver boards shown below.
a. Note: only 4 of the stepper driver boards require a 2pin female header.

### 11. Place the power and fan terminal blocks into their appropriate holes. Bend their pins

to hold them in place and solder them as shown below.

12. Place an electrolytic capacitor in its dedicated holes as shown below.
a. Note: Electrolytic capacitors MUST be oriented correctly. If they are not they will boil and explode. PAY CAREFUL ATTENTION THAT THE NEGATIVE WIRE IS PLACED IN THE NEGATIVE HOLE AND THE POSITIVE WIRE IS PLACED IN THE POSITIVE HOLE AS SHOWN BELOW.

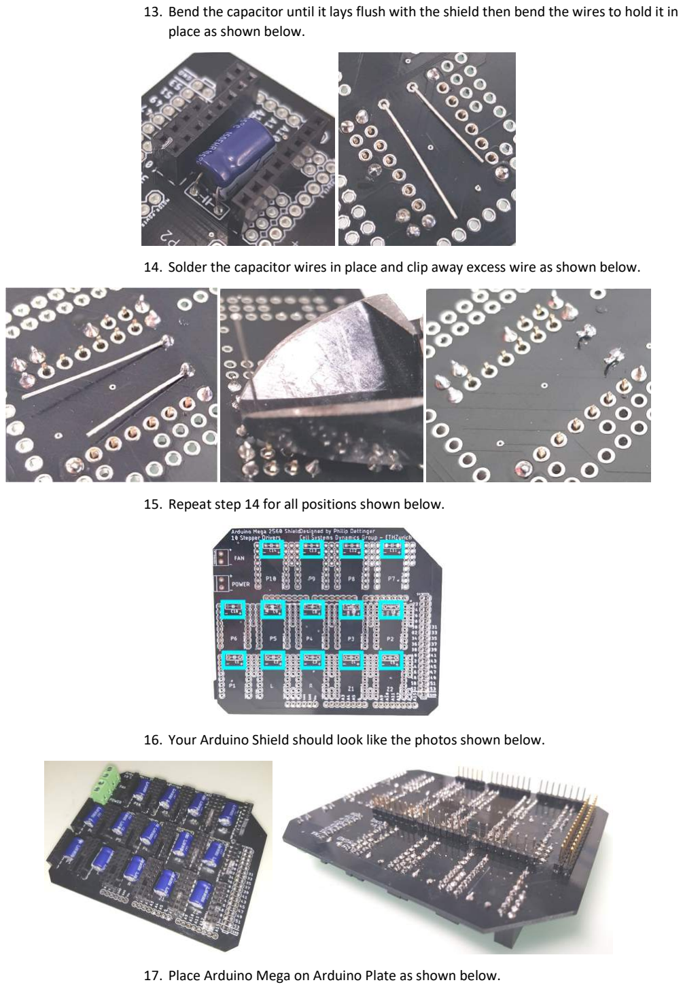
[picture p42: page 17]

13. Bend the capacitor until it lays flush with the shield then bend the wires to hold it in place as shown below.
14. Solder the capacitor wires in place and clip away excess wire as shown below.
15. Repeat step 14 for all positions shown below.
16. Your Arduino Shield should look like the photos shown below.
17. Place Arduino Mega on Arduino Plate as shown below.

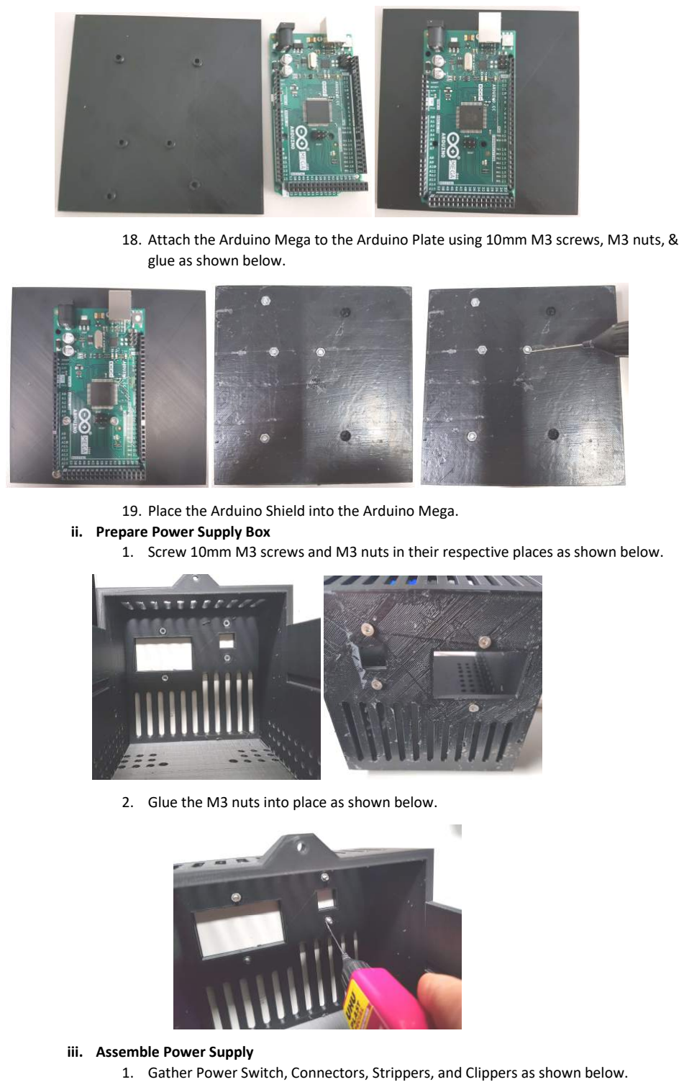
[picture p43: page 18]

### 18. Attach the Arduino Mega to the Arduino Plate using 10mm M3 screws, M3 nuts, &

glue as shown below.

19. Place the Arduino Shield into the Arduino Mega.
ii. Prepare Power Supply Box
1. Screw 10mm M3 screws and M3 nuts in their respective places as shown below.
2. Glue the M3 nuts into place as shown below.

iii. Assemble Power Supply
1. Gather Power Switch, Connectors, Strippers, and Clippers as shown below.

2. Clip off paddle connectors as shown below.
3. Strip wires 5mm from tip as shown below.
4. Insert bare wires into shovel connectors and solder as shown below.
5. Insert power switch in the front panel of the box as shown below.

6. Loosen screws in the L, N, & GND positions of the power supply as shown below.

### 7. Place shovel connectors for L (Red), N (Black), and GND (Yellow/Green) in their

respective locations and tighten their screws as shown below.

### 8. Connect V+ wire from the power supply to (+) power on the Arduino Shield and V-

wire from the power supply to (-) power on the Arduino Shield as shown below.
9. Use 10mm M4 screws to connect the Power Supply to the box as shown below.

### 10. Connect V+ wire (Red) from the Fan to (+) fan on the Arduino Shield and V- wire

(Black) from the Fan to (-) fan on the Arduino Shield as shown below.

### 11. Place Stepper Drivers into Driver ports according to your planned number of stepper

drivers as shown below.
a. NOTE: Pay close attention to their orientation of the Stepper drivers. The ENA pin must be in the upper right corner as shown below.

### 12. Thread Stepper Motor Cables through their holes in the Power Box and connect

them to the Arduino Shield as shown below.
13. Repeat Step 11 for the limit switch cables as shown below.
14. Place the Arduino Plate in its slot as shown below.

### 15. Connect the Fan to the right half of the Power Box using 25mm M3 screws and M3

nuts as shown below.

### 16. Close the Power Box and fix the Power Supply using 10mm M4 screws as shown

below.

17. Attach the handle to the box using 20mm M3 Screws and M3 nuts as shown below.

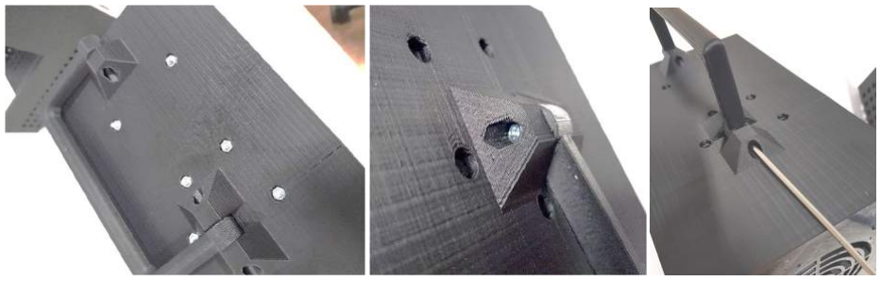
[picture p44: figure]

e. Install Arduino Sketch
i. Download Arduino IDE https://www.arduino.cc/en/software ii. Connect to Arduino MEGA with USB cable.
iii. Open Arduino IDE.
iv. Open PHIL_14SM_210216 sketch.
v. Select the correct port for connecting to the Arduino MEGA from Tools > Port

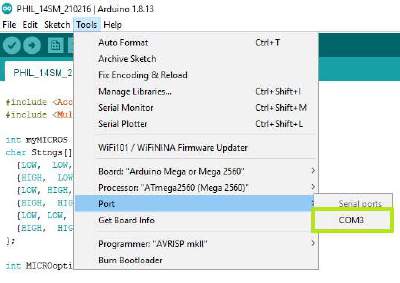
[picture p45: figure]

vi. Click “Upload.”

### 2. Set Up PHIL

a. Place PHIL on desired surface.
b. Fix PHIL in place with 4x 10mm M3 screws if placed on a microscope as shown below.

c. Connect Power Control Box to stepper motors and limit switches as shown below.
d. Plug remaining stepper motor cables into peristaltic pumps as shown below.
i. Note: All stepper motor cables must be plugged into a stepper motor to avoid damaging stepper motor drivers. Any stepper motor can be used for this purpose even if it is not to be utilized for pumping.

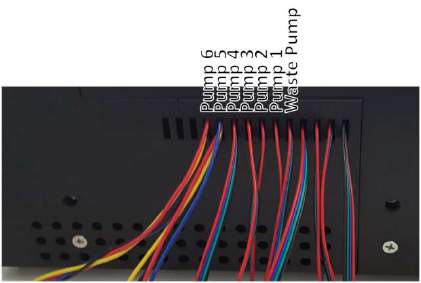
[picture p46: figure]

e. Plug power cord and USB into Power Control Box as shown below.
f. Plug power cord into power source and USB into the computer to be utilized for control.

### 3. Appendix 1: Basic Soldering

a. Useful resources:

i. https://www.instructables.com/How-to-solder/ii. https://www.youtube.com/watch?v=Zu3TYBs65FM
iii. https://electronicsclub.info/soldering.htm
iv. https://www.wikihow.com/Solder-Wires-Together
v. https://uk.rs-online.com/web/generalDisplay.html?id=ideas-and-advice/how-to-solder-guide
b. Safety Precautions
i. Soldering irons heat to >300°C. Never touch the tip with bare skin.
ii. Soldering irons heat to >300°C. Never place them on combustible surfaces.
iii. Soldering irons heat to >300°C. Hold them securely by the handle.
iv. Solder often contains lead and produces smoke. Always solder in a well-ventilated area.
v. Liquid solder is >300°C and can drip. Clear your soldering area of debris before soldering. vi. Liquid solder is >300°C and can drip. Wear the appropriate personal protective equipment (goggles, gloves, and a lab coat).
vii. Soldering irons heat to >300°C. Always treat a soldering iron as though it were hot.

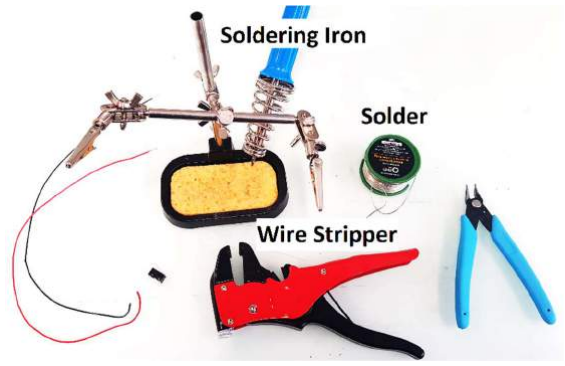
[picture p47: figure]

c. Step by Step
i. Preheat your soldering iron by plugging it in to a power outlet.
ii. Check the temperature by touching the tip to a wet sponge.
iii. “Wet” the tip with solder as shown below.
1. Note: If solder does not melt instantaneously, wait 1 minute and try again.

iv. Strip 5mm of wire insulation as shown below.

v. Splice the exposed wire with the joint as shown below.

vi. Place your soldering iron tip to the spliced join and apply solder until all exposed metal has been covered and a secure joint is formed as shown below.

vii. Wipe your soldering iron on a wet sponge to clean excess solder and flux as shown below.

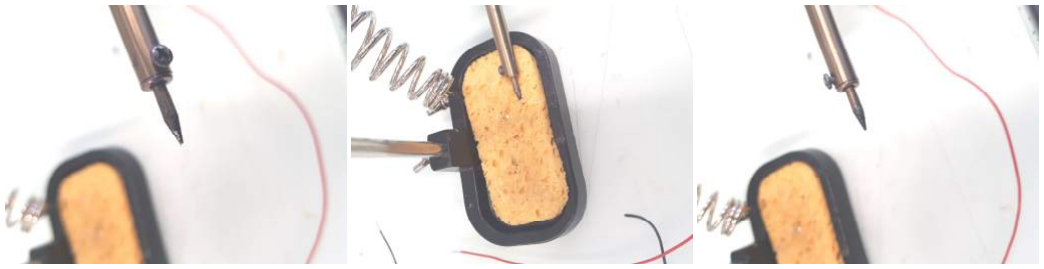
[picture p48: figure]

viii. Repeat as necessary.

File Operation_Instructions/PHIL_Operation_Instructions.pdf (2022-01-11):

PHIL Operation

### 1. Operate PHIL

a. Start GUI
i. Open latest GUI version.
ii. Run GUI script.
iii. Select Configuration File or click cancel to generate a new one. iv. Click “Detect Port,” if necessary.
v. Select Arduino Port.
vi. Click “Connect.”
vii. After connection is acknowledged click “Home.”

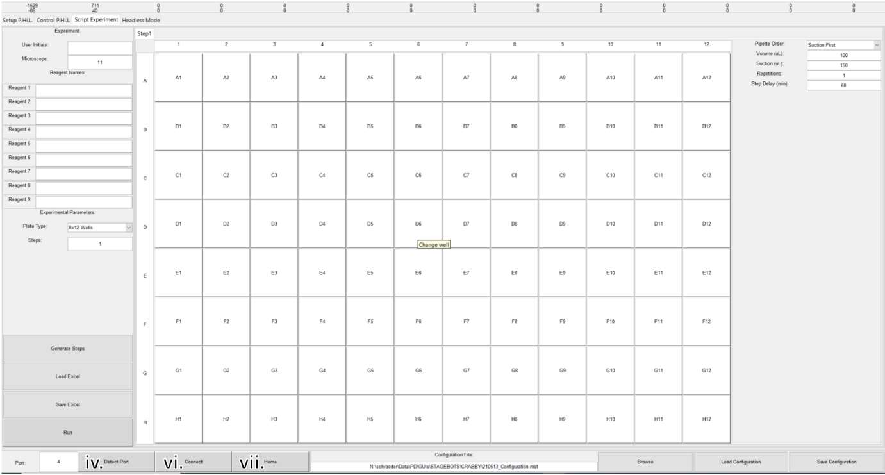
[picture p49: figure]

b. Calibrate Robot
i. Place a 96 well plate in the stage.
ii. Move the robot to your desired wells.
iii. For each well:
1. When the pipet tips are above each well enter an estimated offset.

### 2. Click “Go to Offset.” 3. If you are satisfied with the adjustment click “Set offset” 4. If you are not satisfied with the adjustment click “Go back” and enter

new offset values.
iv. Click any well.
v. Click “Go to Well Bottom.”
vi. Adjust the pipet height up or down. vii. When satisfied click “Set Well Bottom.”

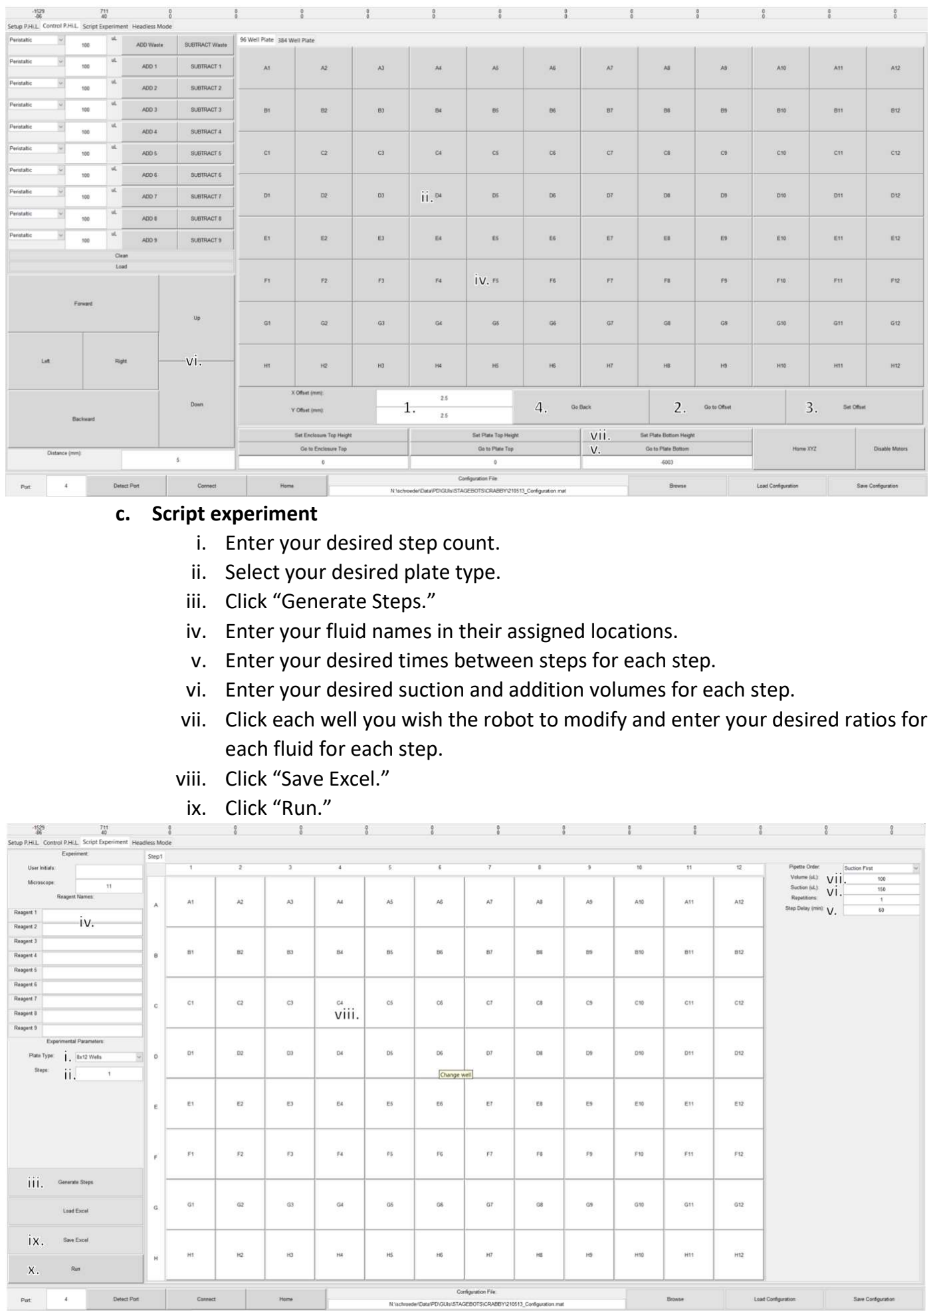
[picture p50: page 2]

c. Script experiment
i. Enter your desired step count.
ii. Select your desired plate type.
iii. Click “Generate Steps.”
iv. Enter your fluid names in their assigned locations.
v. Enter your desired times between steps for each step.
vi. Enter your desired suction and addition volumes for each step.
vii. Click each well you wish the robot to modify and enter your desired ratios for each fluid for each step.
viii. Click “Save Excel.”
ix. Click “Run.”

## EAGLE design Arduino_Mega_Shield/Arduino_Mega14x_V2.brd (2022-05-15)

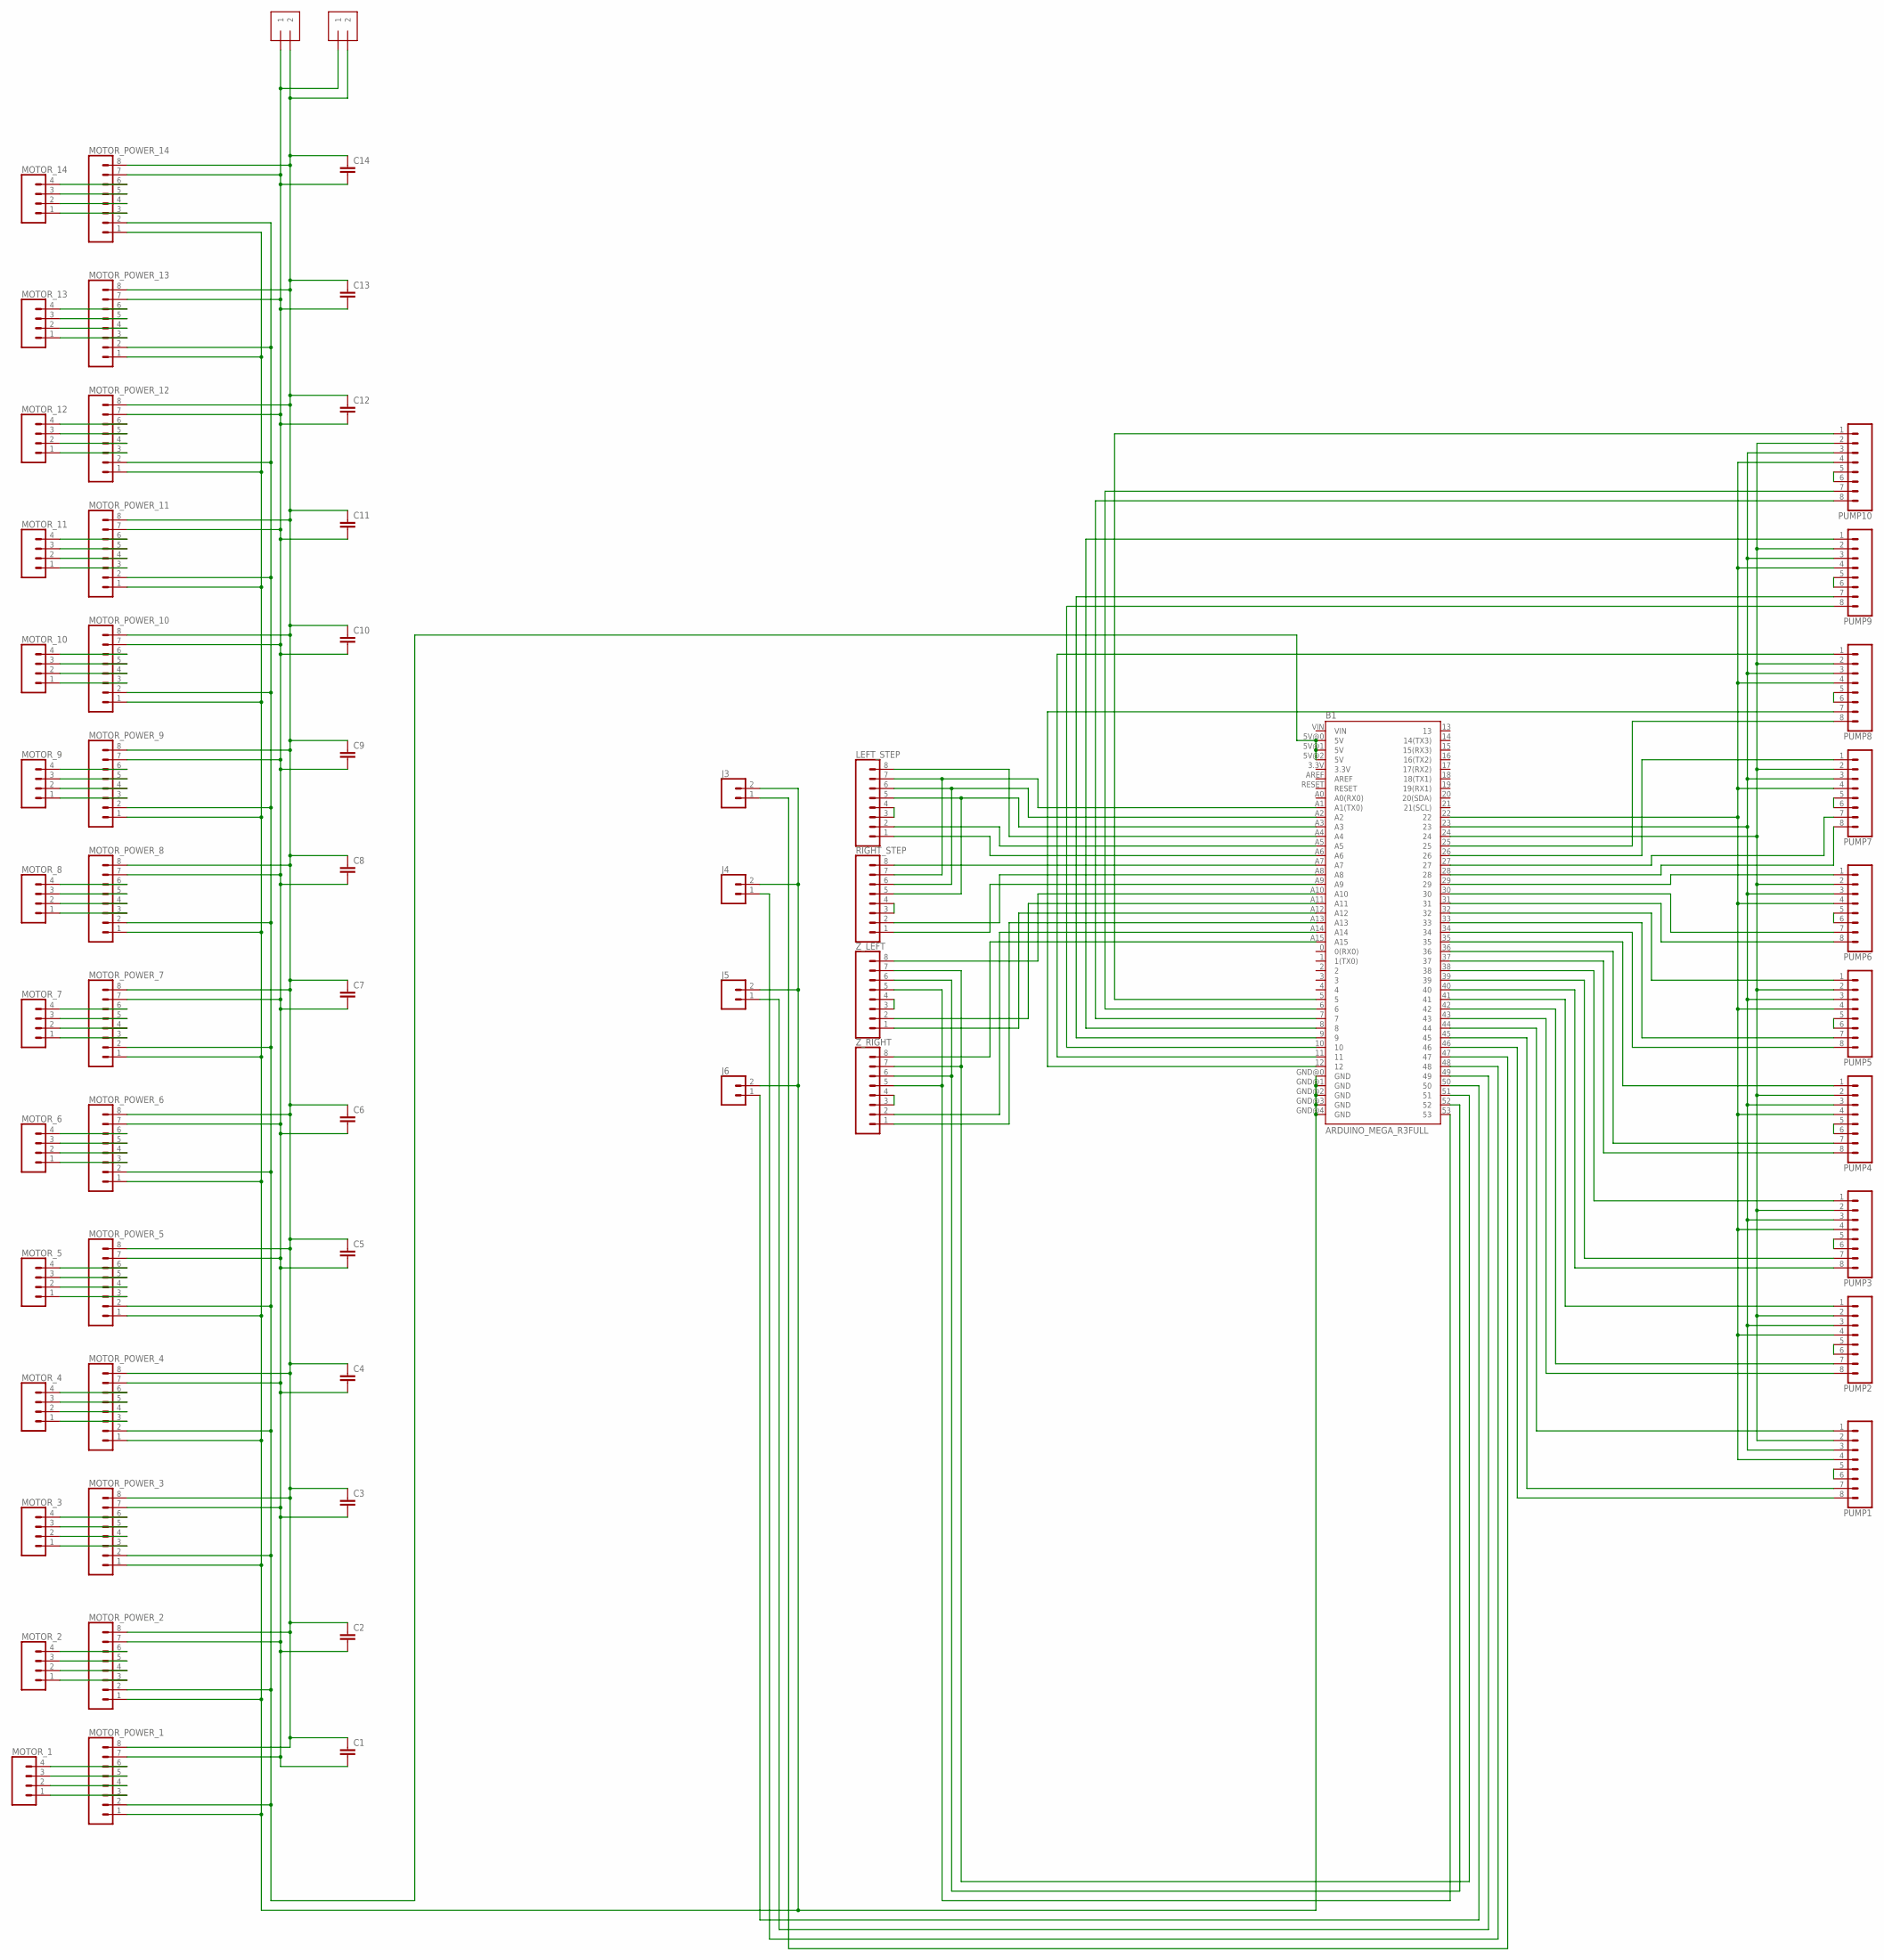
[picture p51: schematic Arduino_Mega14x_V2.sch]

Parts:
B1: ARDUINO_MEGA_R3FULL; ARDUINO_MEGA
C1, C2, C3, C4, C5, C6, C7, C8, C9, C10, C11, C12, C13, C14: C5/2.5; C5B2.5
J1, J2: 1X2-3.5MM
J3, J4, J5, J6: CONN_02; 1X02
LEFT_STEP: CONN_08"; 1X08
MOTOR_1, MOTOR_2, MOTOR_3, MOTOR_4, MOTOR_5, MOTOR_6, MOTOR_7, MOTOR_8, MOTOR_9, MOTOR_10, MOTOR_11, MOTOR_12, MOTOR_13, MOTOR_14: CONN_04; 1X04
MOTOR_POWER_1, MOTOR_POWER_2, MOTOR_POWER_3, MOTOR_POWER_4, MOTOR_POWER_5, MOTOR_POWER_6, MOTOR_POWER_7, MOTOR_POWER_8, MOTOR_POWER_9, MOTOR_POWER_10, MOTOR_POWER_11, MOTOR_POWER_12, MOTOR_POWER_13, MOTOR_POWER_14: CONN_08"; 1X08
PUMP1, PUMP2, PUMP3, PUMP4, PUMP5, PUMP6, PUMP7, PUMP8, PUMP9, PUMP10: CONN_08"; 1X08
RIGHT_STEP: CONN_08"; 1X08
Z_LEFT: CONN_08"; 1X08
Z_RIGHT: CONN_08"; 1X08

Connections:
unnamed: MOTOR_1.1, MOTOR_POWER_1.3
unnamed: MOTOR_1.2, MOTOR_POWER_1.4
unnamed: MOTOR_1.3, MOTOR_POWER_1.5
unnamed: LEFT_STEP.3, LEFT_STEP.4
unnamed: MOTOR_1.4, MOTOR_POWER_1.6
unnamed: MOTOR_2.1, MOTOR_POWER_2.3
unnamed: MOTOR_2.2, MOTOR_POWER_2.4
unnamed: RIGHT_STEP.3, RIGHT_STEP.4
unnamed: MOTOR_2.3, MOTOR_POWER_2.5
unnamed: MOTOR_2.4, MOTOR_POWER_2.6
unnamed: MOTOR_3.1, MOTOR_POWER_3.3
unnamed: MOTOR_3.2, MOTOR_POWER_3.4
unnamed: MOTOR_3.3, MOTOR_POWER_3.5
unnamed: MOTOR_3.4, MOTOR_POWER_3.6
unnamed: MOTOR_4.1, MOTOR_POWER_4.3
unnamed: MOTOR_4.2, MOTOR_POWER_4.4
unnamed: MOTOR_4.3, MOTOR_POWER_4.5
unnamed: Z_LEFT.3, Z_LEFT.4
unnamed: MOTOR_4.4, MOTOR_POWER_4.6
unnamed: MOTOR_5.1, MOTOR_POWER_5.3
unnamed: MOTOR_5.2, MOTOR_POWER_5.4
unnamed: MOTOR_5.3, MOTOR_POWER_5.5
unnamed: MOTOR_5.4, MOTOR_POWER_5.6
unnamed: MOTOR_6.1, MOTOR_POWER_6.3
unnamed: Z_RIGHT.3, Z_RIGHT.4
unnamed: MOTOR_6.2, MOTOR_POWER_6.4
unnamed: PUMP1.5, PUMP1.6
unnamed: MOTOR_6.3, MOTOR_POWER_6.5
unnamed: MOTOR_6.4, MOTOR_POWER_6.6
unnamed: MOTOR_7.1, MOTOR_POWER_7.3
unnamed: MOTOR_7.2, MOTOR_POWER_7.4
unnamed: PUMP2.5, PUMP2.6
unnamed: MOTOR_7.3, MOTOR_POWER_7.5
unnamed: MOTOR_7.4, MOTOR_POWER_7.6
unnamed: PUMP3.5, PUMP3.6
unnamed: MOTOR_8.1, MOTOR_POWER_8.3
unnamed: MOTOR_8.2, MOTOR_POWER_8.4
unnamed: MOTOR_8.3, MOTOR_POWER_8.5
unnamed: MOTOR_8.4, MOTOR_POWER_8.6
unnamed: PUMP4.5, PUMP4.6
unnamed: MOTOR_9.1, MOTOR_POWER_9.3
unnamed: MOTOR_9.2, MOTOR_POWER_9.4
unnamed: MOTOR_9.3, MOTOR_POWER_9.5
unnamed: PUMP5.5, PUMP5.6
unnamed: MOTOR_9.4, MOTOR_POWER_9.6
unnamed: MOTOR_10.1, MOTOR_POWER_10.3
unnamed: MOTOR_10.2, MOTOR_POWER_10.4
unnamed: PUMP6.5, PUMP6.6
unnamed: MOTOR_10.3, MOTOR_POWER_10.5
unnamed: MOTOR_10.4, MOTOR_POWER_10.6
unnamed: MOTOR_11.1, MOTOR_POWER_11.3
unnamed: PUMP7.5, PUMP7.6
unnamed: MOTOR_11.2, MOTOR_POWER_11.4
unnamed: MOTOR_11.3, MOTOR_POWER_11.5
unnamed: MOTOR_11.4, MOTOR_POWER_11.6
unnamed: PUMP8.5, PUMP8.6
unnamed: MOTOR_12.1, MOTOR_POWER_12.3
unnamed: MOTOR_12.2, MOTOR_POWER_12.4
unnamed: MOTOR_12.3, MOTOR_POWER_12.5
unnamed: PUMP9.5, PUMP9.6
unnamed: MOTOR_12.4, MOTOR_POWER_12.6
unnamed: MOTOR_13.1, MOTOR_POWER_13.3
unnamed: MOTOR_13.2, MOTOR_POWER_13.4
unnamed: PUMP10.5, PUMP10.6
unnamed: MOTOR_13.3, MOTOR_POWER_13.5
unnamed: MOTOR_13.4, MOTOR_POWER_13.6
unnamed: MOTOR_14.1, MOTOR_POWER_14.3
unnamed: MOTOR_14.2, MOTOR_POWER_14.4
unnamed: MOTOR_14.3, MOTOR_POWER_14.5
unnamed: MOTOR_14.4, MOTOR_POWER_14.6
unnamed: B1.GND@0 (GND), B1.GND@1 (GND), B1.GND@2 (GND), B1.GND@3 (GND), B1.GND@4 (GND), J3.2, J4.2, J5.2, J6.2, MOTOR_POWER_1.1, MOTOR_POWER_2.1, MOTOR_POWER_3.1, MOTOR_POWER_4.1, MOTOR_POWER_5.1, MOTOR_POWER_6.1, MOTOR_POWER_7.1, MOTOR_POWER_8.1, MOTOR_POWER_9.1, MOTOR_POWER_10.1, MOTOR_POWER_11.1, MOTOR_POWER_12.1, MOTOR_POWER_13.1, MOTOR_POWER_14.1
unnamed: B1.A1 (A1(TX0)), LEFT_STEP.7, RIGHT_STEP.7
unnamed: B1.A2, LEFT_STEP.6, RIGHT_STEP.6
unnamed: B1.A3, LEFT_STEP.5, RIGHT_STEP.5
unnamed: B1.51, Z_LEFT.7, Z_RIGHT.7
unnamed: B1.52, Z_LEFT.6, Z_RIGHT.6
unnamed: B1.53, Z_LEFT.5, Z_RIGHT.5
unnamed: B1.22, PUMP1.4, PUMP2.4, PUMP3.4, PUMP4.4, PUMP5.4, PUMP6.4, PUMP7.4, PUMP8.4, PUMP9.4, PUMP10.4
unnamed: B1.23, PUMP1.3, PUMP2.3, PUMP3.3, PUMP4.3, PUMP5.3, PUMP6.3, PUMP7.3, PUMP8.3, PUMP9.3, PUMP10.3
unnamed: B1.24, PUMP1.2, PUMP2.2, PUMP3.2, PUMP4.2, PUMP5.2, PUMP6.2, PUMP7.2, PUMP8.2, PUMP9.2, PUMP10.2
unnamed: B1.A15, Z_RIGHT.8
unnamed: B1.5V@0 (5V), B1.5V@1 (5V), B1.5V@2 (5V), MOTOR_POWER_1.2, MOTOR_POWER_2.2, MOTOR_POWER_3.2, MOTOR_POWER_4.2, MOTOR_POWER_5.2, MOTOR_POWER_6.2, MOTOR_POWER_7.2, MOTOR_POWER_8.2, MOTOR_POWER_9.2, MOTOR_POWER_10.2, MOTOR_POWER_11.2, MOTOR_POWER_12.2, MOTOR_POWER_13.2, MOTOR_POWER_14.2
unnamed: C1.2, C2.2, C3.2, C4.2, C5.2, C6.2, C7.2, C8.2, C9.2, C10.2, C11.2, C12.2, C13.2, C14.2, J1.1, J2.1, MOTOR_POWER_1.7, MOTOR_POWER_2.7, MOTOR_POWER_3.7, MOTOR_POWER_4.7, MOTOR_POWER_5.7, MOTOR_POWER_6.7, MOTOR_POWER_7.7, MOTOR_POWER_8.7, MOTOR_POWER_9.7, MOTOR_POWER_10.7, MOTOR_POWER_11.7, MOTOR_POWER_12.7, MOTOR_POWER_13.7, MOTOR_POWER_14.7
unnamed: C1.1, C2.1, C3.1, C4.1, C5.1, C6.1, C7.1, C8.1, C9.1, C10.1, C11.1, C12.1, C13.1, C14.1, J1.2, J2.2, MOTOR_POWER_1.8, MOTOR_POWER_2.8, MOTOR_POWER_3.8, MOTOR_POWER_4.8, MOTOR_POWER_5.8, MOTOR_POWER_6.8, MOTOR_POWER_7.8, MOTOR_POWER_8.8, MOTOR_POWER_9.8, MOTOR_POWER_10.8, MOTOR_POWER_11.8, MOTOR_POWER_12.8, MOTOR_POWER_13.8, MOTOR_POWER_14.8
unnamed: B1.A14, Z_RIGHT.2
unnamed: B1.A13, Z_RIGHT.1
unnamed: B1.A12, Z_LEFT.1
unnamed: B1.A11, Z_LEFT.2
unnamed: B1.A10, Z_LEFT.8
unnamed: B1.A9, RIGHT_STEP.1
unnamed: B1.A8, RIGHT_STEP.2
unnamed: B1.A7, RIGHT_STEP.8
unnamed: B1.A6, LEFT_STEP.1
unnamed: B1.A5, LEFT_STEP.2
unnamed: B1.A4, LEFT_STEP.8
unnamed: B1.50, J6.1
unnamed: B1.49, J5.1
unnamed: B1.48, J4.1
unnamed: B1.47, J3.1
unnamed: B1.46, PUMP1.8
unnamed: B1.45, PUMP1.7
unnamed: B1.44, PUMP1.1
unnamed: B1.43, PUMP2.8
unnamed: B1.42, PUMP2.7
unnamed: B1.41, PUMP2.1
unnamed: B1.40, PUMP3.8
unnamed: B1.39, PUMP3.7
unnamed: B1.38, PUMP3.1
unnamed: B1.37, PUMP4.8
unnamed: B1.36, PUMP4.7
unnamed: B1.35, PUMP4.1
unnamed: B1.34, PUMP5.8
unnamed: B1.33, PUMP5.7
unnamed: B1.32, PUMP5.1
unnamed: B1.31, PUMP6.8
unnamed: B1.30, PUMP6.7
unnamed: B1.29, PUMP6.1
unnamed: B1.28, PUMP7.8
unnamed: B1.27, PUMP7.7
unnamed: B1.26, PUMP7.1
unnamed: B1.25, PUMP8.8
unnamed: B1.12, PUMP8.7
unnamed: B1.11, PUMP8.1
unnamed: B1.10, PUMP9.8
unnamed: B1.9, PUMP9.7
unnamed: B1.8, PUMP9.1
unnamed: B1.7, PUMP10.8
unnamed: B1.6, PUMP10.7
unnamed: B1.5, PUMP10.1

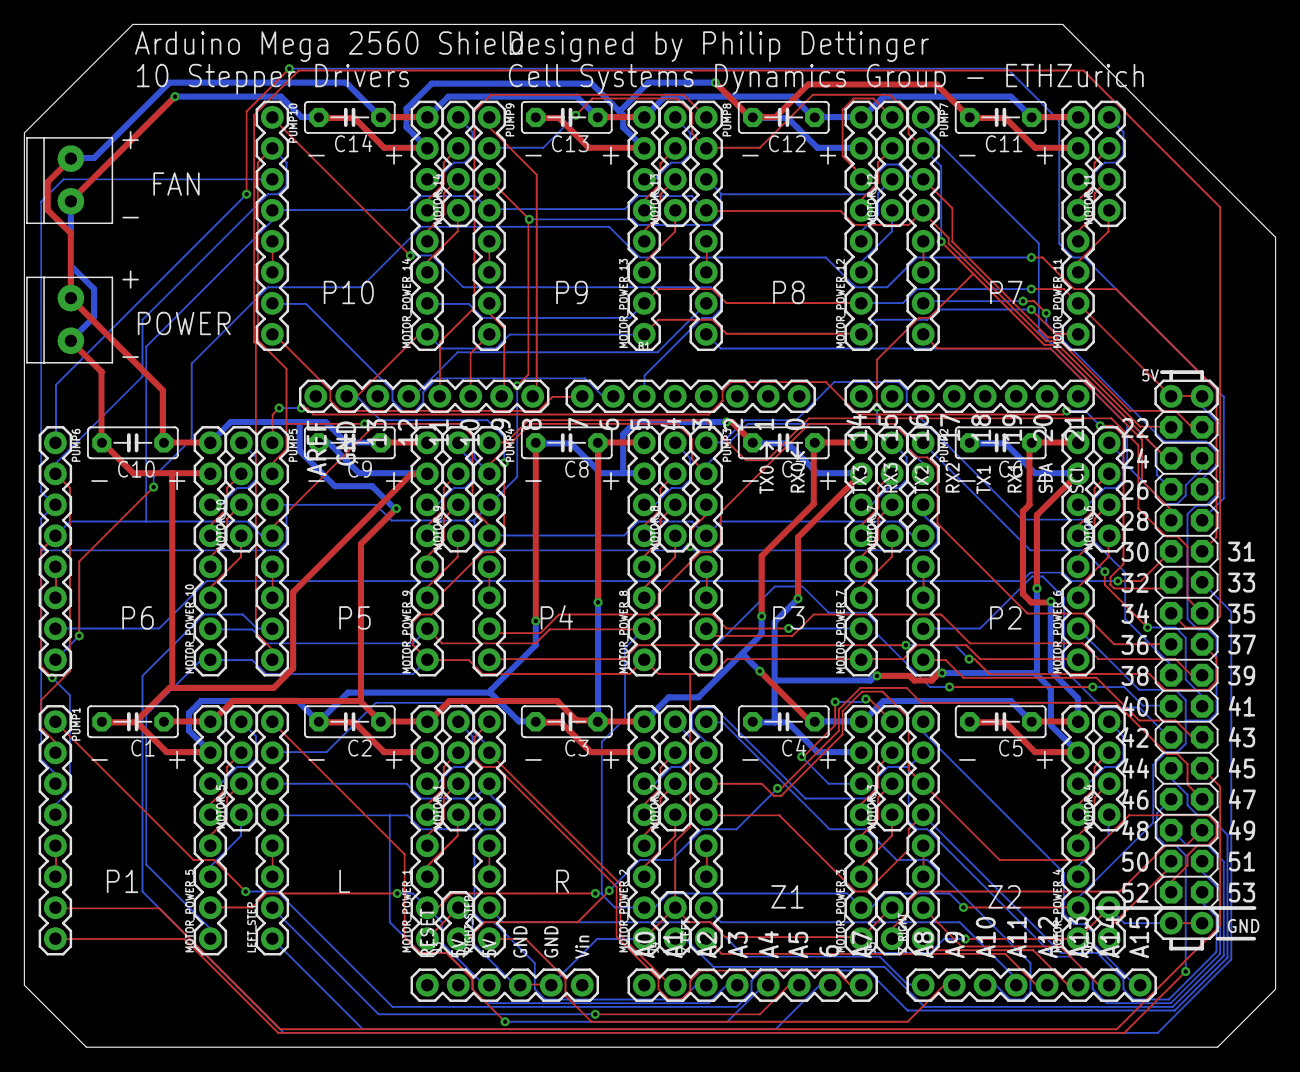
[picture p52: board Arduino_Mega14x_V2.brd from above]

Board: 2 copper layers, 102.5 x 83.8 mm, 63 parts (0 on the bottom side), 129 nets.

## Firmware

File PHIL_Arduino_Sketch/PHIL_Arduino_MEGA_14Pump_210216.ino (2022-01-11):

#include <AccelStepper.h>
#include <MultiStepper.h>

int myMICROS = 1;
char Sttngs[][3] = {
  {LOW,  LOW, LOW}, // Full step
  {HIGH,  LOW, LOW}, // Half step
  {LOW, HIGH,  LOW}, // 1/4 step
  {HIGH,  HIGH,  LOW}, // 1/8 step
  {LOW, LOW, HIGH}, // 1/16 step
  {HIGH,  HIGH,  HIGH}
};

int MICROoptions[] = {1, 2, 4, 8, 16, 32};

//Stepper  L R Z1 Z2 V P1 P2 P3 P4 P5  P6  P7  P8  P9
int enaPINS[] = {69,  64,  61,  58,  44,  41,  38,  35,  32,  29,  26,  11,  8, 5};
int dirPINS[] = {67,  66,  63,  60,  46,  43,  40,  37,  34,  31,  28,  25,  10,  7};
int stpPINS[] = {68,  65,  62,  59,  45,  42,  39,  36,  33,  30,  27,  12,  9, 6};
int M1[] = {51,  51,  55,  55,  24,  24,  24,  24,  24,  24,  24,  24,  24,  24};
int M2[] = {52,  52,  56,  56,  23,  23,  23,  23,  23,  23,  23,  23,  23,  23};
int M3[] = {53,  53,  57,  57,  22,  22,  22,  22,  22,  22,  22,  22,  22,  22};
int limPins[] = {50,  49,  48,  47};

AccelStepper stepperL(1, stpPINS[0], dirPINS[0]);
AccelStepper stepperR(1, stpPINS[1], dirPINS[1]);
AccelStepper stepperZ1(1, stpPINS[2], dirPINS[2]);
AccelStepper stepperZ2(1, stpPINS[3], dirPINS[3]);
AccelStepper stepperV(1, stpPINS[4], dirPINS[4]);
AccelStepper stepper1(1, stpPINS[5], dirPINS[5]);
AccelStepper stepper2(1, stpPINS[6], dirPINS[6]);
AccelStepper stepper3(1, stpPINS[7], dirPINS[7]);
AccelStepper stepper4(1, stpPINS[8], dirPINS[8]);
AccelStepper stepper5(1, stpPINS[9], dirPINS[9]);
AccelStepper stepper6(1, stpPINS[10], dirPINS[10]);
AccelStepper stepper7(1, stpPINS[11], dirPINS[11]);
AccelStepper stepper8(1, stpPINS[12], dirPINS[12]);
AccelStepper stepper9(1, stpPINS[13], dirPINS[13]);

int limitSwitchL = limPins[0]; // Target Limit Switch L
int limitSwitchR = limPins[1]; // Target Limit Switch R
int limitSwitchZ1 = limPins[2]; // Target Limit Switch Z
int limitSwitchZ2 = limPins[3]; // Target Limit Switch Z

String readString; //main captured String
String Comm;
String Lstr;
String Rstr;
String Z1str;
String Z2str;
String Vstr;
String str1;
String str2;
String str3;
String str4;
String str5;
String str6;
String str7;
String str8;
String str9;

long Lint;
long Rint;
long Z1int;
long Z2int;
long Vint;
long int1;
long int2;
long int3;
long int4;
long int5;
long int6;
long int7;
long int8;
long int9;

int ind0;
int indL;
int indR;
int indZ1;
int indZ2;
int indV;
int ind1;
int ind2;
int ind3;
int ind4;
int ind5;
int ind6;
int ind7;
int ind8;
int ind9;

int MAXspd = 6400;
int MAXaccl = 6400;

void setup() {
  // put your setup code here, to run once:
  pinMode(limitSwitchL, INPUT_PULLUP);
  //digitalWrite(limitSwitchL, HIGH);
  pinMode(limitSwitchR, INPUT_PULLUP);
  //digitalWrite(limitSwitchR, HIGH);
  pinMode(limitSwitchZ1, INPUT_PULLUP);
  //digitalWrite(limitSwitchZ1, HIGH);
  pinMode(limitSwitchZ2, INPUT_PULLUP);
  //digitalWrite(limitSwitchZ2, HIGH);

  stepperL.setMaxSpeed(MAXspd * myMICROS);
  stepperR.setMaxSpeed(MAXspd * myMICROS);
  stepperZ1.setMaxSpeed(MAXspd * myMICROS);
  stepperZ2.setMaxSpeed(MAXspd * myMICROS);
  stepperV.setMaxSpeed(MAXspd * myMICROS);
  stepper1.setMaxSpeed(MAXspd * myMICROS);
  stepper2.setMaxSpeed(MAXspd * myMICROS);
  stepper3.setMaxSpeed(MAXspd * myMICROS);
  stepper4.setMaxSpeed(MAXspd * myMICROS);
  stepper5.setMaxSpeed(MAXspd * myMICROS);
  stepper6.setMaxSpeed(MAXspd * myMICROS);
  stepper7.setMaxSpeed(MAXspd * myMICROS);
  stepper8.setMaxSpeed(MAXspd * myMICROS);
  stepper9.setMaxSpeed(MAXspd * myMICROS);
  stepperL.setAcceleration(MAXaccl * myMICROS);
  stepperR.setAcceleration(MAXaccl * myMICROS);
  stepperZ1.setAcceleration(MAXaccl * myMICROS);
  stepperZ2.setAcceleration(MAXaccl * myMICROS);
  stepperV.setAcceleration(MAXaccl * myMICROS);
  stepper1.setAcceleration(MAXaccl * myMICROS);
  stepper2.setAcceleration(MAXaccl * myMICROS);
  stepper3.setAcceleration(MAXaccl * myMICROS);
  stepper4.setAcceleration(MAXaccl * myMICROS);
  stepper5.setAcceleration(MAXaccl * myMICROS);
  stepper6.setAcceleration(MAXaccl * myMICROS);
  stepper7.setAcceleration(MAXaccl * myMICROS);
  stepper8.setAcceleration(MAXaccl * myMICROS);
  stepper9.setAcceleration(MAXaccl * myMICROS);

  for (int i = 0; i <= 13; i++) {
    pinMode(enaPINS[i], OUTPUT);
    digitalWrite(enaPINS[i], HIGH);
    pinMode(dirPINS[i], OUTPUT);
    pinMode(stpPINS[i], OUTPUT);
    pinMode(M1[i], OUTPUT);
    digitalWrite(M1[i], HIGH);
    pinMode(M2[i], OUTPUT);
    digitalWrite(M2[i], HIGH);
    pinMode(M3[i], OUTPUT);
    digitalWrite(M3[i], HIGH);
  }
  Serial.begin(9600);
  Serial.println("E+0+0+0+0+0+0+0+0+0+0+0+0+0+0*"); // so I can keep track of what is loaded
}

void MOVE(long Lint, long Rint, long Z1int, long Z2int, long Vint, long int1, long int2, long int3, long int4, long int5, long int6, long int7, long int8, long int9) {
  Serial.println("Here0");
  stepperL.setCurrentPosition(0);
  stepperR.setCurrentPosition(0);
  stepperZ1.setCurrentPosition(0);
  stepperZ2.setCurrentPosition(0);
  stepperV.setCurrentPosition(0);
  stepper1.setCurrentPosition(0);
  stepper2.setCurrentPosition(0);
  stepper3.setCurrentPosition(0);
  stepper4.setCurrentPosition(0);
  stepper5.setCurrentPosition(0);
  stepper6.setCurrentPosition(0);
  stepper7.setCurrentPosition(0);
  stepper8.setCurrentPosition(0);
  stepper9.setCurrentPosition(0);
  MultiStepper steppers;
  int count = 0;
  if (Lint != 0) {
    steppers.addStepper(stepperL);
    count = count + 1;
  }
  if (Rint != 0) {
    steppers.addStepper(stepperR);
    count = count + 1;
  }
  if (Z1int != 0) {
    steppers.addStepper(stepperZ1);
    count = count + 1;
  }
  if (Z2int != 0) {
    steppers.addStepper(stepperZ2);
    count = count + 1;
  }
  if (Vint != 0) {
    steppers.addStepper(stepperV);
    count = count + 1;
  }
  if (int1 != 0) {
    steppers.addStepper(stepper1);
    count = count + 1;
  }
  if (int2 != 0) {
    steppers.addStepper(stepper2);
    count = count + 1;
  }
  if (int3 != 0) {
    steppers.addStepper(stepper3);
    count = count + 1;
  }
  if (int4 != 0) {
    steppers.addStepper(stepper4);
    count = count + 1;
  }
  if (int5 != 0) {
    steppers.addStepper(stepper5);
    count = count + 1;
  }
  if (int6 != 0) {
    steppers.addStepper(stepper6);
    count = count + 1;
  }
  if (int7 != 0) {
    steppers.addStepper(stepper7);
    count = count + 1;
  }
  if (int8 != 0) {
    steppers.addStepper(stepper8);
    count = count + 1;
  }
  if (int9 != 0) {
    steppers.addStepper(stepper9);
    count = count + 1;
  }
  long positions[count]; // Array of desired stepper positions
  count = 0;
  if (Lint != 0) {
    positions[count] = Lint;
    count = count + 1;
  }
  if (Rint != 0) {
    positions[count] = Rint;
    count = count + 1;
  }
  if (Z1int != 0) {
    positions[count] = Z1int;
    count = count + 1;
  }
  if (Z2int != 0) {
    positions[count] = Z2int;
    count = count + 1;
  }
  if (Vint != 0) {
    positions[count] = Vint;
    count = count + 1;
  }
  if (int1 != 0) {
    positions[count] = int1;
    count = count + 1;
  }
  if (int2 != 0) {
    positions[count] = int2;
    count = count + 1;
  }
  if (int3 != 0) {
    positions[count] = int3;
    count = count + 1;
  }
  if (int4 != 0) {
    positions[count] = int4;
    count = count + 1;
  }
  if (int5 != 0) {
    positions[count] = int5;
    count = count + 1;
  }
  if (int6 != 0) {
    positions[count] = int6;
    count = count + 1;
  }
  if (int7 != 0) {
    positions[count] = int7;
    count = count + 1;
  }
  if (int8 != 0) {
    positions[count] = int8;
    count = count + 1;
  }
  if (int9 != 0) {
    positions[count] = int9;
    count = count + 1;
  }
  steppers.moveTo(positions);
  steppers.runSpeedToPosition();
  Serial.println("MDONE");
}

void ENABLE(long Lint, long Rint, long Z1int, long Z2int, long Vint, long int1, long int2, long int3, long int4, long int5, long int6, long int7, long int8, long int9) {
  int nbls[] = {Lint, Rint, Z1int, Z2int, Vint, int1, int2, int3, int4, int5, int6, int7, int8, int9};
  for (int i = 0; i <= 13; i++) {
    if (nbls[i] != 0) {
      digitalWrite(enaPINS[i], LOW);
      Serial.println("LOW");
    }
    else {
      digitalWrite(enaPINS[i], HIGH);
      Serial.println("HIGH");
    }
  }
  Serial.println("EDONE");
}

void SPEED(long Lint, long Rint, long Z1int, long Z2int, long Vint, long int1, long int2, long int3, long int4, long int5, long int6, long int7, long int8, long int9) {
  stepperL.setMaxSpeed(Lint);
  stepperR.setMaxSpeed(Rint);
  stepperZ1.setMaxSpeed(Z1int);
  stepperZ2.setMaxSpeed(Z2int);
  stepperV.setMaxSpeed(Vint);
  stepper1.setMaxSpeed(int1);
  stepper2.setMaxSpeed(int2);
  stepper3.setMaxSpeed(int3);
  stepper4.setMaxSpeed(int4);
  stepper5.setMaxSpeed(int5);
  stepper6.setMaxSpeed(int6);
  stepper7.setMaxSpeed(int7);
  stepper8.setMaxSpeed(int8);
  stepper9.setMaxSpeed(int9);
}

void ACCELERATION(long Lint, long Rint, long Z1int, long Z2int, long Vint, long int1, long int2, long int3, long int4, long int5, long int6, long int7, long int8, long int9) {
  stepperL.setAcceleration(Lint);
  stepperR.setAcceleration(Rint);
  stepperZ1.setAcceleration(Z1int);
  stepperZ2.setAcceleration(Z2int);
  stepperV.setAcceleration(Vint);
  stepper1.setAcceleration(int1);
  stepper2.setAcceleration(int2);
  stepper3.setAcceleration(int3);
  stepper4.setAcceleration(int4);
  stepper5.setAcceleration(int5);
  stepper6.setAcceleration(int6);
  stepper7.setAcceleration(int7);
  stepper8.setAcceleration(int8);
  stepper9.setAcceleration(int9);
}

void HOME(long Lint, long Rint, long Z1int, long Z2int, long Vint, long int1, long int2, long int3, long int4, long int5, long int6, long int7, long int8, long int9) {
    stepperL.setMaxSpeed(MAXspd * myMICROS);
  stepperR.setMaxSpeed(MAXspd * myMICROS);
  stepperZ1.setMaxSpeed(MAXspd * myMICROS);
  stepperZ2.setMaxSpeed(MAXspd * myMICROS);

  stepperL.setAcceleration(MAXaccl * myMICROS);
  stepperR.setAcceleration(MAXaccl * myMICROS);
  stepperZ1.setAcceleration(MAXaccl * myMICROS);
  stepperZ2.setAcceleration(MAXaccl * myMICROS);
  
  stepperL.setCurrentPosition(0);
  stepperR.setCurrentPosition(0);
  stepperZ1.setCurrentPosition(0);
  stepperZ2.setCurrentPosition(0);
  
  stepperL.moveTo(Lint);
  stepperR.moveTo(Rint);
  stepperZ1.moveTo(Z1int);
  stepperZ2.moveTo(Z2int);
  Serial.println("Here0");

  if (Lint != 0) {
    while (stepperL.distanceToGo() != 0 && digitalRead(limitSwitchL) == HIGH) {
      stepperL.run();
      Serial.println("Here1");
    }
  }

  Serial.println("Here2");

  if (Rint != 0) {
    while (stepperR.distanceToGo() != 0 && digitalRead(limitSwitchR) == HIGH) {
      stepperR.run();
      Serial.println("Here3");
    }
  }

  Serial.println("Here4");

  if (Z1int != 0 && Z2int != 0) {
    while (stepperZ1.distanceToGo() != 0 || stepperZ2.distanceToGo() != 0) {
      if (digitalRead(limitSwitchZ1) == HIGH && stepperZ1.distanceToGo() != 0) {
        stepperZ1.run();
        Serial.println("Here5");
      } else {
        stepperZ1.setCurrentPosition(0);
        stepperZ1.moveTo(0);
      }
      if (digitalRead(limitSwitchZ2) == HIGH && stepperZ2.distanceToGo() != 0) {
        stepperZ2.run();
        Serial.println("Here6");
      } else {
        stepperZ2.setCurrentPosition(0);
        stepperZ2.moveTo(0);
      }
    }
  }

  Serial.println("Here7");
}
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

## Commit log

2022-05-15 Add files via upload
    Updated Arduino shield
    [Arduino_Mega14x_V2.brd, Arduino_Mega14x_V2.sch]
2022-05-20 Add files via upload
    Updated Arduino sketch which fixes a bug in the command string processing loop.

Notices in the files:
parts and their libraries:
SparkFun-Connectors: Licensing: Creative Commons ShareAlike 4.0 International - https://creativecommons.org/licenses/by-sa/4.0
